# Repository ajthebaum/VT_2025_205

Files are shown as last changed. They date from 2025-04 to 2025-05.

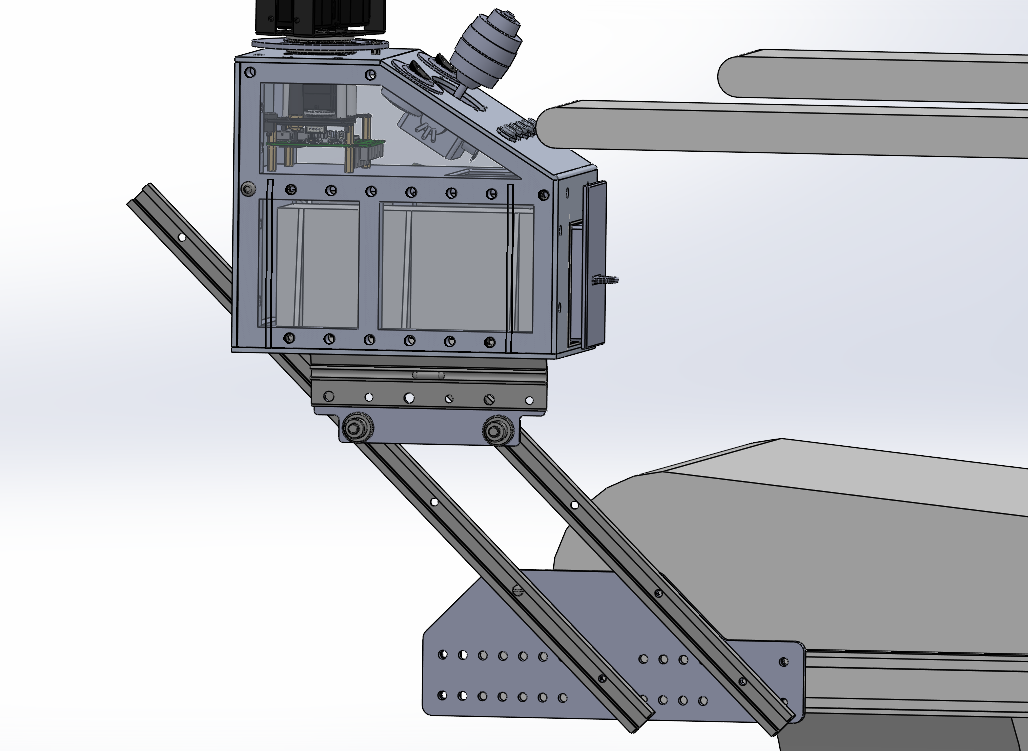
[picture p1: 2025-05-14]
CADFiles&Drawings/DXF and PDF Files/Reference Images/Fullview.png

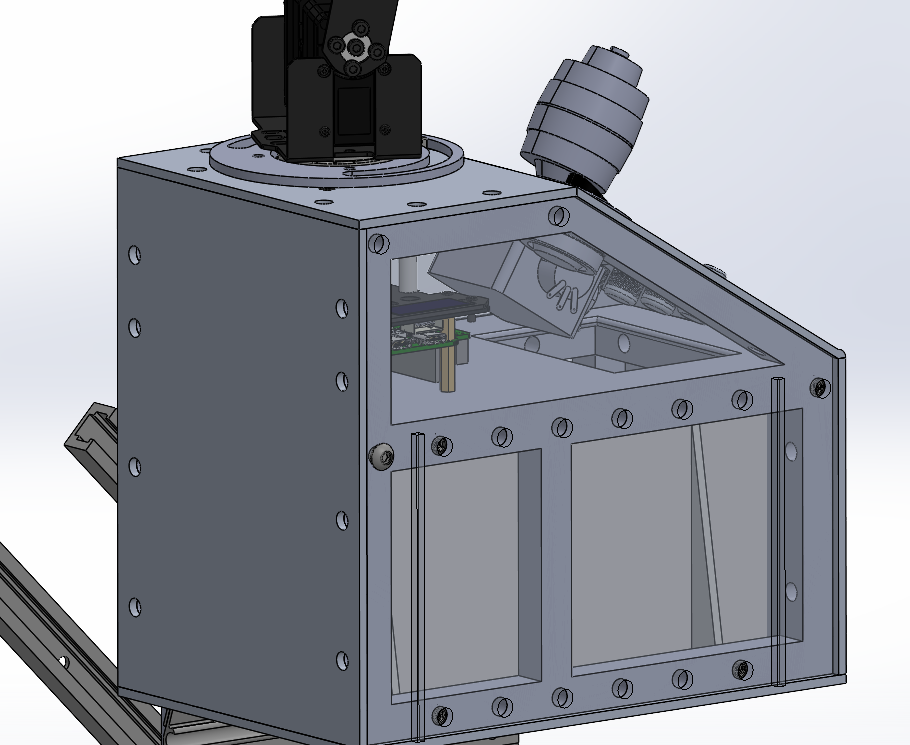
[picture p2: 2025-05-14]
CADFiles&Drawings/DXF and PDF Files/Reference Images/CaseView3.png

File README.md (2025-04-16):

# VT_2025_205
A collection of files for those interested in VT's team 205 Senior Design Project for the 2024-2025 year

VT's senior design team 205 is sponsored by Parent Project Muscular Dystrophy (PPMD). Our goal is to modify an off 
the shelf robotic arm for use on common motorized wheelchairs used by people with Duchenne muscular dystrophy (DMD).
It is intended for the project to continue past our senior year, and continue to refine and improve, as well as introduce new 
functions that may be of high value to people with DMD.

Currently, we are using the Waveshare Ro-Arm M2S, as well as an adafruit feather v2 along with a joystick, buttons,
switches, and LEDs. We are programming on the feather, formatting a JSON document that is sent over serial communication to
the board found on the Ro-Arm M2S, which then deserializes the JSON document and performs the corresponding robotic arm movement.
The code found on the Ro-Arm M2S board is provided by the manufacturer, and found in this repository is the code the team used
on the feather to read analog and digital signals and perform logic to update local coordinates.

We are not programmers, and have no formal training in programming (we're all ME's). There are refinements that can be made to our code that can 
significantly improve it, and we urge you to do so. We'd love to see this project continue, and see how people improve and adapt what we have done
to new problems, or new designs. Additionally, we are new to GitHub and are learning as we go. Feedback and advice are appreciated as we have a lot
to learn!

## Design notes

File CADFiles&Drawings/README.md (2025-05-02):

This folder contains the CAD parts, assemblies, drawimgs, and other files that were used to create the physical system that mounts on the wheelchair.
It may be necessary to rebuild the assemblies, refer to the assembly manual to see how its put together

These parts will be uploaded as we get time and once the final deliverables have been made

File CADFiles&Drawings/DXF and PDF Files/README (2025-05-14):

Files used for manufacturing parts on the laser cutter, CNC mill, and plasma cutter

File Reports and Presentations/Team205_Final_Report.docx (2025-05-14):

Proceedings of the 2025 Virginia Tech

Mechanical Engineering Senior Capstone Exposition

VTMECAP-2025

May 6, 2025, Blacksburg, Virginia, USA

VTMECAP-2025-205

# Assistive Robotic Aid for People with Duchenne Muscular DystrophY

Brooke Harrington¹, Cavan Moriarty¹, Omar Abuljobain¹, Justin Lee¹, Andrew Baum¹

¹Department of Mechanical Engineering, Virginia Tech, Blacksburg, VA

Abstract

DMD is a genetic disorder commonly found in men that deteriorates muscle tissue as they age, which progressively reduces mobility and requires those affected to use motorized wheelchairs for daily travel [1]. In addition to motorized wheelchairs, young adults with DMD often need devices that assist with upper body mobility. People with DMD would value an affordable, easy to control assistive robot that mounts on their wheelchair and provides two high value functions: operating elevator and handicap door buttons and bringing a drink to the user’s face.

To provide the two high value functions, team 205 utilized an off-the-shelf robotic arm, an Adafruit Feather V2 microcontroller, a joystick, buttons, switches, and other key electronics to develop a prototype for an affordable assistive robotic. Additionally, common materials and manufacturing methods were used such as 3-D printing, CNC milling, and laser cutters, to manufacture a mounting/containment structure for the assistive device. A prototype was fabricated, tested, and revised to ensure the device could accomplish the high value functions.

Team testing showed that the prototype met the requirements developed while conceptualizing a design, as well as user requirements such as size, safety, and functionality. Additionally, the prototype is able to complete its functions on instruments complaint with standards (minimum door width, button height requirements). End user testing showed that the prototype could complete the two high value functions, while being easier to control than other options on the market. Though the prototype was able to complete the two high value functions, improvements can be made that elevate user experience, ease of operation of the device, and sophistication of device functionality.

Nomenclature

3D Three Dimensional

ADA Americans with Disabilities Act

ANSYS Analysis System

CNC Computer Numerical Control

DMD Duchenne Muscular Dystrophy

DOF Degrees of Freedom

ESP Electronic Stability Program

FBD Free Body Diagram

FEA Finite Element Analysis

FOS Factor of Safety

GPIO General Purpose Input-Output

JSON JavaScript Object Notation

LED Light Emitting Diode

PCB Printable Circuit Board

PVC Polyvinyl Chloride

PPMD Parent Project Muscular Dystrophy

ROM Range of Motion

SPST Single Pole Single Throw

TR Technical Requirement

UI User Interface

1. INTRODUCTION

PPMD is a nonprofit organization that has been leading the fight against DMD since 1994, whose leading goal has been to ensure afflicted families have access to the latest assistive technologies through investment in research and development of pharmaceuticals and medical devices [1]. To help reach this goal, PPMD has sponsored senior design team 205 to develop an affordable and easy-to-use robotic aid by modifying a low-cost robotic arm and mounting it to commonly used wheelchairs. Although assistive devices may take various forms, the most optimal design was determined to be a robotic arm because of its ability to perform two high value functions: pushing an elevator/handicap button and retrieving a drink. Current robotic arms on the market that directly address DMD are often too expensive, some exceeding sixty-thousand dollars, and are difficult to control with more than six DOF [2]. Therefore, team 205 will provide users with DMD the key functions they require at a substantially lower cost with a less complex method of operation via a lower DOF system.

To simplify the design process of an assistive robotic device that could achieve the high value functions, the system was divided into three main subsystems: mechanical, electronic, and software. The mechanical subsystem included designing a mounting assembly that attaches the robotic system to a Permobil wheelchair, the most common wheelchair used in the DMD community. Additionally, the mechanical subsystem involved designing a case for sensitive electronics that also acted as a platform for the low-cost robotic arm and UI. The electronics subsystem consists of the RoArm’s PCB, the Adafruit Feather and protoboard, the UI (switches, buttons, joystick and LED), and the battery. When assembled, these components allow power to be distributed and used for control logic of the robotic arm. Lastly, the software subsystem found on the Feather reads signals from the UI and completed all necessary logic to update the coordinates, which were then formatted and sent to the RoArm PCB to be used for motor control. The software was also used to optimize control of the robotic arm and provide programmable functions desired by the end user.

Additionally, the team had to meet specific requirements determined by members from PPMD. The first requirement stated that the motorized wheelchair with the robotic system attached shall fit through an ADA compliant door, which has a minimum clearance width of thirty-two inches [3]. Second, the attached robotic system shall be able to press an ADA compliant elevator button and handicap door button, which are positioned between 35 and 48 in from the ground [4]. Third, the robotic arm and case shall be water resistant in the event that the user is caught in a rainstorm. Lastly, the system shall be easily attached and detached from the motorized wheelchair for transportation.

2. MATERIALS AND METHODS
  2.1 Mechanical
    2.1.1 Manufacturing Processes

Multiple manufacturing processes were required to fabricate the mounting and robotic system. For mounting, both the sliding and connecting plate were cut from an aluminum panel by a plasma cutter and CNC mill. Alternatively, acrylic panels were cut into their respective shapes using a laser cutter. Lastly, 3D-printing with ABS filament was used to create the required parts with varying infills and purposes.

3D-printed parts include the corner frame, battery case and cover, waterproofing well, cylindrical guide, end effector cover, pin, stopping plate, and armrest attachment. The battery case encapsulates the battery, which maintains its position at the lower half of the electronics housing by bolting to the bottom acrylic panel. The battery cover, waterproofing well, cylindrical guide, and end effector cover serve to waterproof exposed electronics by sheltering them or guiding water away from the electronics. The stopping plate was glued to the base servo-plate and provided a guide for a standoff. The standoff, bolted into the top of the electronics case, stopped the arm from rotating to undesired angles by colliding with the stopping plate, providing a mechanical safeguard as shown in Figure 1.

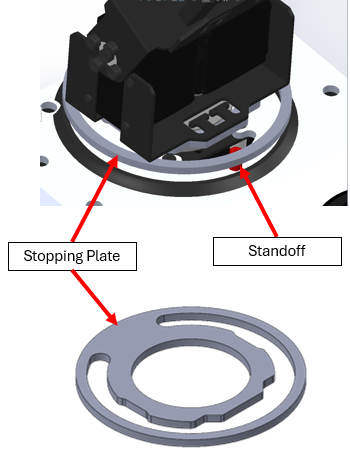
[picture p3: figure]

Figure 1: Mechanical Safeguard

Lastly, the armrest is an optional attachment that can be put in place of the front acrylic panel to provide support to the user’s arm during operation.

    2.1.2 Mounting

A Unitrack is a linear slide bolted to the side of a Permobil wheelchair, allowing for many extensions and attachments to be added. The mounting system is designed for quick, direct attachment to the Unitrack; however, the team only had access to a Jazzy motorized wheelchair. Therefore, an additional aluminum L-channel was needed to attach the Unitrack to the Jazzy wheelchair. In the ideal case of a Permobil, the mounting assembly involves a total of four aluminum components as shown in Figure 2: sliding plate, diagonal rails, connecting plate, and French cleats. The sliding plate is the primary point of contact to the Permobil that allows horizontal adjustment of the robotic system. The sliding plate is connected to the Unitrack via wing bolts to allow for easy adjustment and attachment/detachment of the entire robotic system to/from the Permobil. Next, the lower portion of the diagonal rails are attached to the sliding plate via pan head screws at an approximate forty-five-degree angle. The upper portion of the diagonal rails are connected to the connecting plate via a set of three fourths inch diameter locknuts, socket head screws, and square nuts. The connecting plate can slide along the diagonal rails which allows for simultaneous vertical and horizontal adjustment of the robotic system. Lastly, the connecting plate is attached to a pair of French cleats while another set is attached to the electronics case such that the robotic system can be easily removed from the mounting system by simply lifting the electronics case off the French cleats. To prevent the robotic system from being “bumped” off the French cleats, there is a 3D-printed pin that slides through the connecting plate and electronics case.

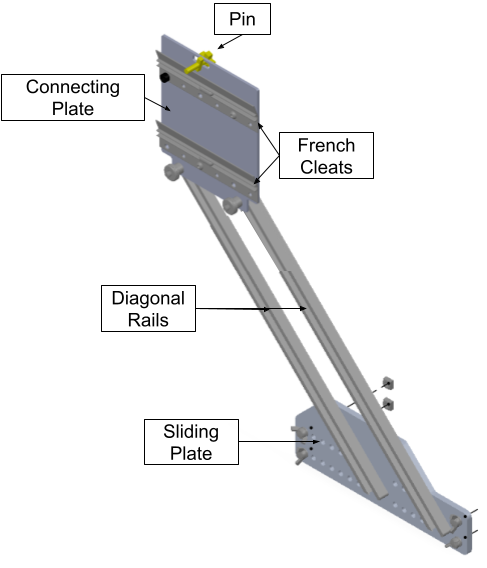
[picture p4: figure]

Figure 2: Mounting Assembly

The process for removing the system off the wheelchair involves removing the key that secures the electronics case and lifting the case off the French cleats. Then, loosening the wing bolts on the sliding plate, and sliding the mounting structure off the Unitrack will completely remove all parts of the system from the wheelchair. With only these two processes, the system is completely removed, meeting the end user requirement of a quickly installed and detachable system.

The ease of attachment for the mounting and robotic system was tested by timing the duration to attach the mounting system to the Unitrack, mounting electronics housing on French cleats, and placing the pin through the connecting plate slot and electronics housing. Ease of detachment was validated by sponsor testing, having a sponsor team member detach the system from the Permobil wheelchair without any prior instructions from the team. The stability of the robotic system in response to the mounting system was evaluated with root cause analysis as well as a sponsor assessment. The root cause analysis involved measuring the deflections of the diagonal rails when the robotic system was attached at different positions. Notably, this test was performed for the team’s Jazzy whilst the sponsor assessment was performed for the sponsor’s Permobil. The assessment involved visual inspection of the robotic systems response to static conditions and dynamic movement of the Permobil. While there were some deflections on the team’s Jazzy wheelchair, there were negligible deflections on the sponsor team’s Permobil wheelchair, which led the team to take no further action when addressing vibration, as it performed within expectations on the intended wheelchair.

    2.1.3 Electronics Casing

The electronics casing houses sensitive electronics, such as the lithium-ion battery, protoboard assembly, and ESP32, in addition to providing mounting points for the robotic arm and UI. The electronics housing is comprised of 3D-printed parts and laser cut acrylic plates.

As shown in Figure 3, the electronics casing has an internal structure that acts as the main point of connection to the robotic arm and acrylic panels. The robotic arm is bolted to the middle plate of the internal structure to a set of standoffs while the acrylic panels bolt to the sides of the internal structure with button head screws. These sides are lined with quarter-inch holes where nut inserts are heated and inserted to provide threading for the button head screws. Furthermore, the internal structure provides adequate space for sliding the protoboard into the pin headers of the ESP32 for a stable connection.

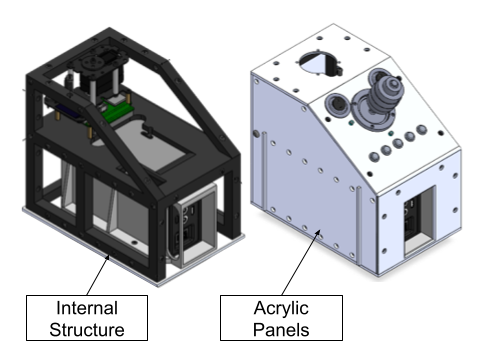
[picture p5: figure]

Figure 3: Electronics Casing

Since the system contains electronics and uses screws as fasteners, it is important to consider the maintenance process to ensure safe operation of the system. All physical components, including the acrylic panels and mounting structure, must be removed and inspected for physical and electric damage. Additionally, the electrical components must be inspected for loose wires, burns, or shorts, and fixed if necessary. Testing will ensure that maintenance activities do not result in system removal from the end user for an extended period, as the end user relies on the system for daily, repetitive tasks. A time limit of three hours was estimated to complete these maintenance activities and tested after full system assembly.

    2.1.4 Robotic Arm

The Waveshare RoArm-M2-S robotic arm was purchased from a third-party vendor and later modified to meet the team’s needs. Initially, the arm was selected as it satisfies the team payload capacity, accuracy at maximum reach, and price requirements. Choosing an arm that satisfied the requirements from the team’s analysis was important in developing a system capable of completing the two high value functions. Once acquired, minor modifications were made such as rotating the end effector ninety degrees as well as rotating the base of the arm ninety degrees to fit the axes of our coordinate system; effectiveness of these changes were verified through testing system operation.

The payload capacity of the end effector was tested by increasing the applied load at the end effector by 100 g each time the robotic arm successfully completed the drinking function; further details on drinking function can be found in Section 2.3. Alternatively, the accuracy of the robotic arm at maximum reach was tested by measuring the horizontal and vertical precision of the end effector position relative to a 35-inch and 48-inch mark. Additional details regarding the test for accuracy can be found in Section 3.2.

    2.1.5 Water-resistant Design

To aid in the water-resistant design of the system, a PVC sleeve, 3D printed end effector cover, 3D printed well, and 3D printed cylindrical sleeve guide were utilized. The end effector cover is meant to protect the end effector servo motor for a short duration in light rainfall. The sleeve acts as an elbow joint cover on its own, but when used with the cylindrical sleeve guide and well, can help protect the lower half of the system, ranging from the elbow servo motor, down to the base servo-motor inside the casing unit.

  2.2 Electrical
    2.2.1 Protoboard

A generic protoboard was used as a connection point for all electronic components which included the ESP32, the Adafruit Feather V2, and the UI. The UI was soldered directly to the protoboard, while the Feather was inserted into corresponding headers that were soldered to the protoboard. Lastly, male headers were soldered to the protoboard and would plug into the female headers of the RoArm PCB, which allowed for serial communication between the Feather and RoArm, and power distribution.

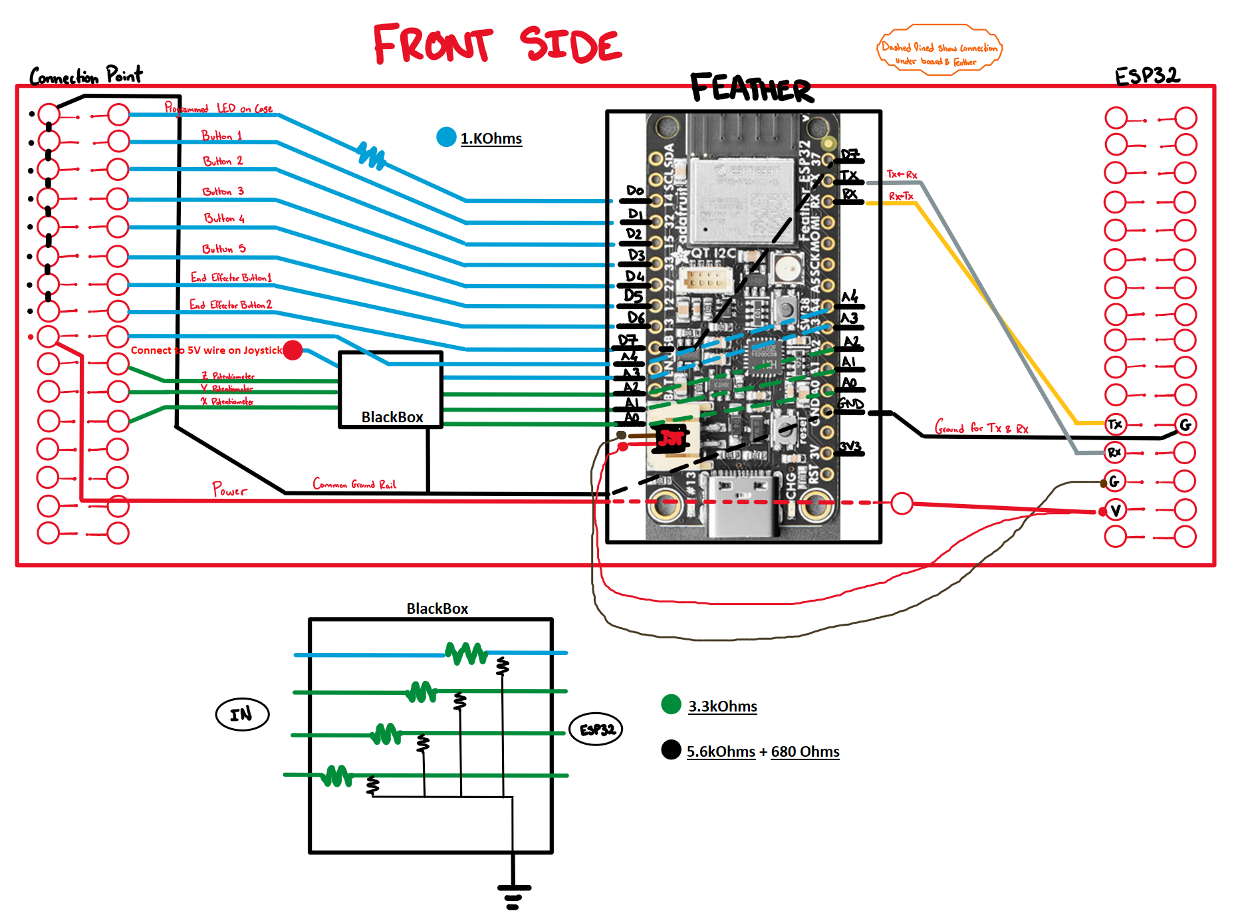
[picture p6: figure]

Figure 4: Protoboard Layout with Feather

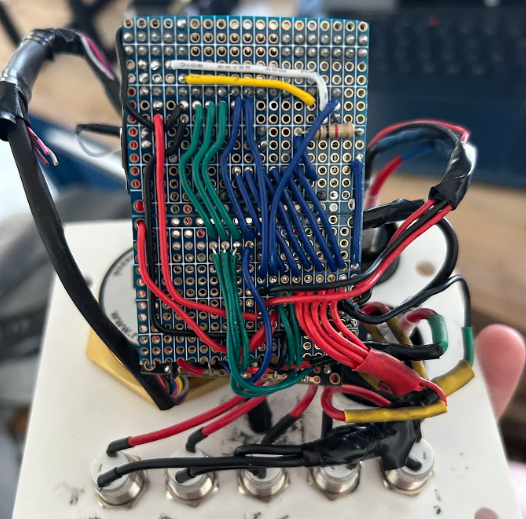
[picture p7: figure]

Figure 5: Protoboard with Solder Connections to Switches, Buttons, and Joystick

    2.2.2 User Interface

The UI contains a three-axis, two-button, Ruffy controls hall effect joystick, five momentary buttons, two SPST switches, and one white LED. Two LEDS beside the switches were removed due to electrical complications that could not be resolved before project completion. The switches were used to enable system and joystick control, and the joystick was used for manual manipulation of the robotic arm. The buttons were used for programming saved locations for later recall, and the LED was used to convey system status to the user. All UI subsystems were mounted on the diagonal plate of the electronics casing, where they would be accessible to the person in the motorized wheelchair as seen in Figure 6.

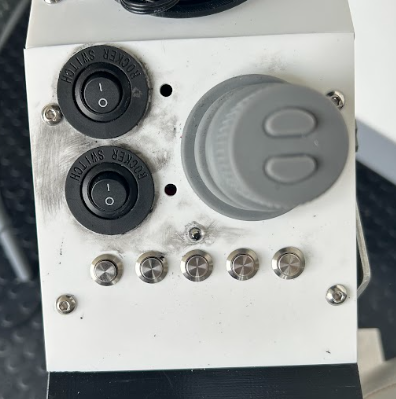
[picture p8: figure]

Figure 6: User Interface (Left – Switches, Right - Joystick, Bottom – Buttons, LED above 3rd button)

    2.2.3 Battery

A 38,400 mAh battery was used to power the robotic arm and all electronics used in the system. The battery is contained in the base of the electronics case and has an LED display showing capacity. The battery also has a switch for powering on and off the system, and a USB port for other attachments. 12 V is routed from the battery to the ESP32 on the robotic arm, which then powers the Feather and protoboard, then the protoboard distributes 3.3 V and 5 V to systems on the UI.

To determine the required battery size, the time at max output and time at minimum output per day were estimated and multiplied by the amperage of these operations then summed to determine the necessary capacity for a battery to last 1 day. Using the frequency of buttons as 30 times a day with a time of 15 sec and the frequency of drink as 30 times per day with a time of 20 secs, max current I of 5 A and min current Imin as 0.2 A, the required battery capacity was determined to be 6200 mAh.

time_(max) = ((freq_b *time_b )+ (freq_w *time_w ))/3600 | (1)
time_(max) =0.2917 hours
time_(min) =24-time_(max) =23.7 hours | (2)
req_(mAh) =((I*time_(max) )+(I_(min) *time_(min) ))*1000 | (3)
req_(mAh) = 6200mAh

The battery selection provides adequate capacity (6.2 times estimated value), which accounts for any differences between estimated values and actual values for the tasks above, and variance in use from different end users.

  2.3 Software
    2.3.1 Waveshare ESP32

The Waveshare RoArm comes equipped with a PCB that contains motor drivers and handles serial communication. This PCB is sold with preinstalled code that can be modified; however, the team opted out of modifying the RoArm code since one of the project goals was to be easily replicable. The code on the RoArm PCB reads a JSON object that contains position data from the serial communication (transfer-TX and receive-RX) pins, which the RoArm then deserializes and turns into motor control. Since the team did not modify this code, an Adafruit Feather V2 microcontroller was used for all logic and coordinate updates.

    2.3.2 Adafruit Feather V2

The Adafruit Feather V2 is an ESP32 based microcontroller equipped with GPIO pins that are used for digital and analog communication with other electronic components. Communication between the Feather and the RoArm PCB uses the “RX” and “TX” pins as seen in Figure 4, which are wired inversely between the boards. The GPIO pins on the Feather are used to take inputs from the switches, joystick, and buttons, and output to the LED. The code on the Feather uses these readings to update the coordinates or call specific functions such as the automatic drink function. Specifically, the joystick is used to manually update the coordinates of the end effector, and the buttons are used to recall specific coordinates that have been previously programmed by the user. Once the user wants to move the end effector, the coordinates are formatted into a JSON object that contains the numeric identifier for the type of control, the cartesian coordinates of the end effector destination, and the speed at which the arm should move. An example is provided below. This data is sent across the serial communication pins, where the RoArm uses the numeric identifier and position data to calculate motor movements. The numeric identifier used for all code on the feather was “1041” or “104”, which specifies that the data contained in the object are x, y, z, and end effector pitch, t, positions (104 allows you to specify a “spd” variable in the object, where 1041 does not, both produce the same linear movement between current and goal points).

The following code is an example of what is written in the Feather:

StaticJsonDocument<200> curposdoc;

curposdoc["T"] = 104;

curposdoc["x"] = curxpos;

curposdoc["y"] = curypos;

curposdoc["z"] = curzpos;

curposdoc["t"] = curtpos;

curposdoc["spd"] = 0.2;

serializeJson(curposdoc, Serial1);

Serial1.println();

What the RoArm receives from the Feather:

{“T”: “104”, “x”: curxpos, “y”: curypos, “z”: curzpos, “t”: curzpos, “spd” = 0.2}

These objects that contain the position data are continuously updated in the Feather and sent to the RoArm to move the end effector position. Optimizations in the code that sync the transfer speed (between the Feather and RoArm) and the coordinate update speed ensure that equal increments of coordinates are sent with each data transfer.

3. RESULTS AND DISCUSSION
  3.1 Results of FEA
    3.1.1 Free Body Diagram

To estimate the mechanical load experienced by the case and mounting structure, a FBD was developed using estimated forces and moments generated during arm operation, which includes the weight of the arm, case, battery, and load, as well as the moments generated by the load and arm and full extension. The model assumed an extreme use test scenario in which the arm is fully extended with a payload at the end effector. This condition was selected to ensure the support structure can withstand maximum mechanical stress.

The total moment applied to the mounting assembly was found to be 4.03 Nm, acting in the counterclockwise direction. The corresponding force at the mounting point, excluding the weight of the case, was determined to be 20.16 N. The contribution of dynamic human interaction was considered negligible in the FBD but was evaluated separately for safety margins. All forces were applied at the interface between the arm base and the vertical support tracks. The calculated forces were then used as the input for subsequent finite element analyses to verify the structural integrity of the electronics casing and mounting assembly under expected operating conditions.

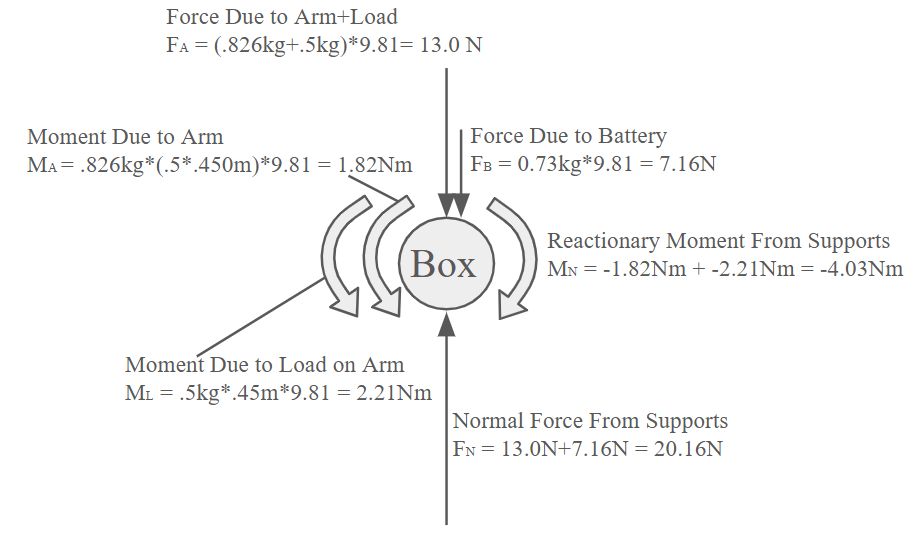
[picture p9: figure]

Figure 7: Free Body Diagram of System

    3.1.2 Engineering Analysis

Following the force and moment estimations from the FBD, a structural FEA was conducted using ANSYS to evaluate stress concentrations and deflection behavior in the electronics casing and mounting assembly. The materials used in the construction were primarily 6061-T6 aluminum alloy, selected for its high strength-to-weight ratio and availability. The alloy has a yield strength of 275.8 MPa, which served as the basis for FOS calculations. Under the maximum loading conditions, the highest observed stress concentration was 48.44 MPa, occurring in the T-track that mounts to the vertical rails as seen in Figure 9. This yielded a conservative FOS of 5.69, which indicated the design was capable of withstanding operational forces without material failure.

Deformation analysis revealed a maximum deflection of 1.62 mm at the edge of the case. This displacement was well within the design tolerance and did not interfere with arm accuracy, which had a resolution requirement of ±10 mm at full extension. Additionally, rotational and positional accuracy for each joint was analyzed based on encoder specifications. The final cumulative error was estimated to be <0.8 mm, confirming that the structural deflection would not compromise system precision. These results validated the mechanical robustness of the mounting architecture and confirmed that the system can maintain both strength and accuracy throughout normal use.

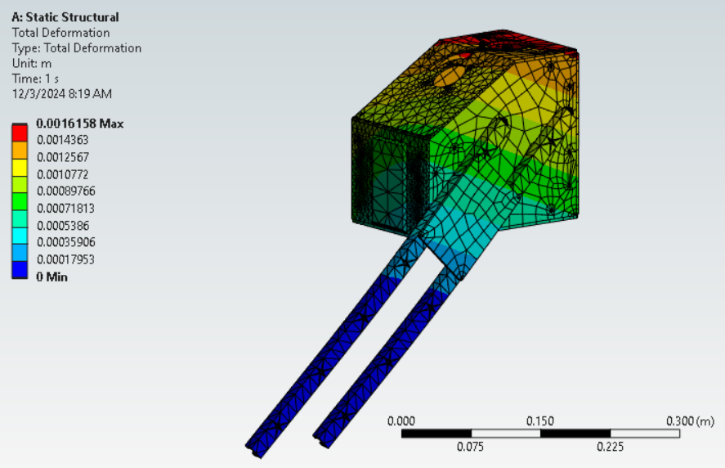
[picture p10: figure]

Figure 8: Ansys Static Structural Analysis of Deformation

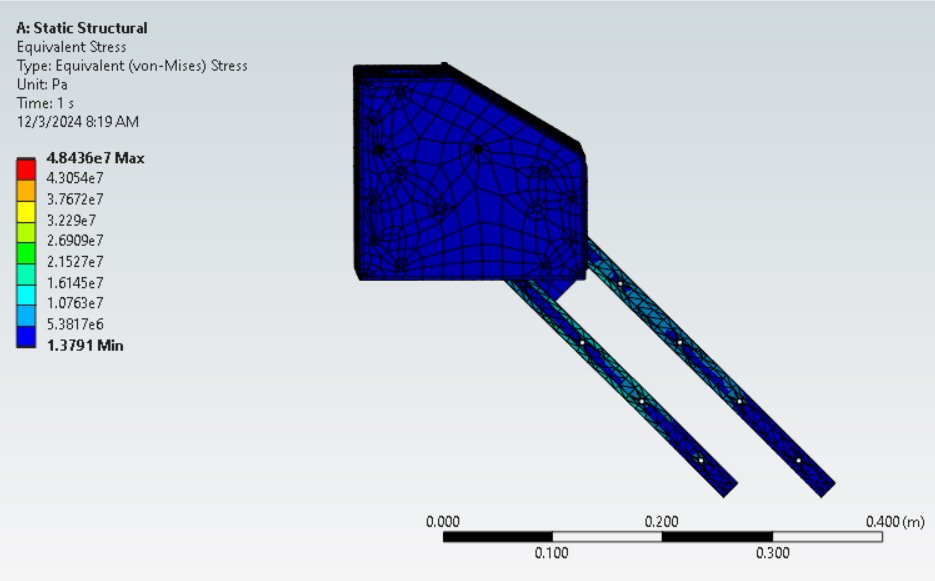
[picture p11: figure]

Figure 9: Ansys Static Structural Analysis of Stress

  3.2 Results of Test Plans
    3.2.1 Installation Test

An installation test was conducted to determine the ease of installation in accordance with TR 3.0.0: The robotic aid shall be installed in less than 1 hr. The test was performed by timing the assembling of the mounting system to the wheelchair Unitrack, placing the French cleats of the electronics casing onto the French cleats of the mounting system, and finally securing the electronics casing to the mounting assembly with the 3D-printed pin. Lower times indicated an easier installation process. The limit for passing this test estimated at 1 hr, and the test was completed in under 1 min at 58.52 secs. This overestimate of installation time was due to multiple design simplifications that improved the installation process by decreasing the amount of assembly required to completely install the system.

    3.2.2 Maintenance Test

A maintenance test was completed to evaluate the time it takes to perform standard maintenance activities, which is important since removal of the system from the user for an extended period of time (3 hrs) is non-ideal, as the user needs the system for daily tasks (TR 3.1.0). Maintenance activities included inspection of all physical structures of the system, inspection of all wire connections and heat shrink, and inspection of the PCB and protoboard for any burnt components. Any damage or broken components that were fixed were included in the test time. The limit for passing was 3 hrs, the expected value was estimated at 1 hr, and the actual value was 22 mins and 53 secs. The system passed the test with a minor electrical tape fix, and it is recommended that a retest be completed after significant use or after six months.

    3.2.3 End Effector Max. Load Capacity Test

The end effector max. load capacity test addresses TR 1.1.4: the arm should be able to bring a drink weighing 470 g to the user, which verifies the robotic arm’s ability to meet the key function of retrieving a drink to the user. This test was performed by increasing the weight of the drink by 100 g every time the robotic arm successfully completed the drinking function. For each execution of the drinking function, a visual inspection of the system’s performance and stability determined whether the robotic arm performed satisfactorily or if the maximum weight limit had been reached.

The results determined that the robotic arm is able to hold a weight of 500 g when extended to its maximum and a weight of 600 g when at close range. Thus, the robotic arm exceeds expectations, meets TR 1.1.4, and is able to successfully retrieve a drink. The weight of the drink includes the combined weight of the liquid, container, and portable cupholder.

    3.2.4 Accuracy Test

An accuracy test was performed to ensure the system was accurate to 10 mm at full extension, stated as requirement TR 1.3.2. This requirement was developed from the ADA button size and height standards, stating the minimum diameter of an elevator button to be ¾ in, and the height from ground to be 35-48 in [4]. This test utilized a tape measure, calipers, the assembled system on a motorized wheelchair, a whiteboard imitating a button wall, tape, and a whiteboard marker to mark the necessary points. At the lowest incremental movement translated from the joystick’s X and Y axis, one unit was moved right from the initial mark set at 35 in from ground. A second point was marked, and the end-effector was once again incrementally moved one unit upward in the Z direction. Once three points were marked, the same procedure was executed 48 in from ground.

Initial results ranged from 5 mm to 14 mm, implying the system can still press ADA complaint buttons; however, it fails the team’s accuracy requirement of 10 mm.

To resolve the initial failure, the speed of position incrementation in the code was changed to 40 ms, such that the incrementation of the position matched the data transfer rate. Syncing these tasks resulted in an accuracy improvement, now ranging from 4 mm to 8 mm, thereby passing the test.

    3.2.5 Restricted Motion Software Safeguards

To ensure safe operation around the user, particularly preventing unintended contact with the user's arm or torso, the team implemented software-based spatial restrictions into the robotic arm’s control system. This safeguard was developed in response to requirement TR 5.2.0, which specifies that the system must include physical or software constraints that prevent the robot from reaching undesired locations. The Feather was programmed to actively monitor the robot’s spatial coordinates—specifically the x, y, and z positions—using magnetic encoder feedback from the Waveshare RoArm motors. The code defines a restricted region in the operating environment, primarily an angular zone ±30° on either side of the UI as seen in Figure 10, where the end effector is prohibited from entering. This safety zone was determined by ergonomic analysis and sponsor feedback, ensuring the robot would never encroach on the user’s hand space during operation.

The restricted motion logic is embedded in the coordinate update routine. If an input command—via joystick or recalled motion function—would move the end effector into a forbidden zone, the command is overridden, and the motion is aborted before transmission to the RoArm system. During the test, the software safeguard was verified across minimum, medium, and maximum speed settings. At all tested velocities and configurations, the robot’s movement remained strictly within allowed regions. As a result, the software safeguard not only fulfilled TR 5.2.0 but also made the reliance on a mechanical limit a redundancy rather than a necessity. The success of this test highlights the effectiveness of embedded software control in maintaining operational safety, especially for users with limited mobility who rely on consistent, predictable system behavior.

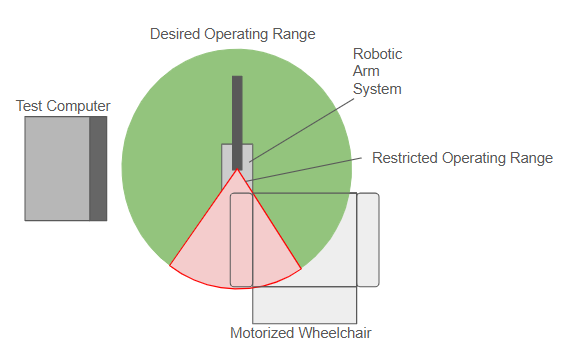
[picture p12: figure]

Figure 10: Diagram of Restricted Motion Test

  3.3 High Value Functions
    3.3.1 Automatic Water Function

An automatic water function was provided in the Feather code, which allows the user to program a “drink” location on the wheelchair and a “user” location where they want the drink to remain for use. The user will additionally program two “safe” points that the system will path through to ensure proper clearance between the drink and the case. Holding the second button on the UI for five seconds will enter “programming” mode for this button, where the user will program these four points. Then pushing the second button momentarily will run the function, moving to the positions saved by the user. Additional logic, such as when to open the end effector and how to move between points, is done within the code and is not programmed by the user. To change this behavior, the user must change the function in the code, which is provided online in a GitHub repository. Currently, the function is operable and works for specific mounting locations of the drink; however, testing on the intended wheelchair was not possible due to mounting interferences with other necessary equipment. Since each person's wheelchair is different, it is ideal to have the cupholder at roughly the same height as the case due to robotic arm capabilities, but more research should be done on an ideal location.

      3.3.1.1 Code Progress

The code is broken into three parts: manual joystick operation, button operations, and safety checks. Manual joystick operation reads the values of the potentiometers in the joystick and compares against limits to increment the local coordinates, which are formatted into a JSON object and sent to the robot.

The button operations use a general button reading function, which passes the button variables into the function, and calls the corresponding programming or recall function for the robot depending on how long the button is pushed for. This framework can be used for additional functions, or to change existing functions, as the movement functions are independent of the button reading framework. Button operation is further discussed in 3.3.2.1.

Lastly, spatial safety features have been implemented to prevent the robot from moving erratically. There are limits on the end effectors maximum and minimum distance from the origin, which prevent the robot from swinging too quickly and hitting other objects or people. There is also a restricted area that spans 60° above the UI as discussed in 3.2.5, which prevents the end effector from hitting the user’s hand while operating the joystick. The last safety measure defines the coordinates of the case and does not allow the end effector to move into this area, so the system does not break itself. Together, these safety features define the operating space of the robot and prevent it from harmfully interacting with itself and its environment.

    3.3.2 Elevator Button Pressing
      3.3.2.1 Ready Positions

One key goal for the system was the ability to store and retrieve position data throughout power cycles. The Arduino “preferences” library was used, which stores data to non-volatile memory using a preferences namespace and keyword. By holding a specific button down for five seconds, the user can enter the “programming” mode and move the arm to the position they would like to store. By pushing the same button momentarily, the user will now store this location and exit programming mode. To recall this position at any time, the user can momentarily push this button, and the arm will move to this stored position. Three buttons are compatible with this operation, firstly, button one programs a “ready” position that is ideally used to move the arm up and in front of the case. Button three and four are used to program two different stow positions. Together, the user can save three unique positions, and one function (automatic drink function), which stores four positions.

      3.3.2.2 Accuracy

Accuracy of the system was a high priority when making design choices, which was reflected during testing through focus on end effector accuracy and spatial safety. The accuracy of our system is determined by three factors: the code, the servo accuracy, and the structural stability of the assembled system. By syncing the coordinate update speed with the data transfer speed, user inputs have been converted to single increments in position data, thereby optimizing the system by preventing overshoot of desired position. Additionally, the distance the joystick is moved from its neutral position is utilized for variable speed control of the robotic arm, where pushing the joystick further from the default position results in quicker movement of the arm.

The Waveshare RoArm was selected because of its servo motor accuracy, advertised to have a resolution of 0.088 ° , translating to a single (base) motor accuracy of ±0.78 mm. As system complexity increases with more motors, the accuracy will likely decrease, but tests show the value remains within the team’s specified accuracy for performing high value functions.

The last factor that effects accuracy is system structural stability, which is a concern for end effector accuracy as the weight shifts or adjusts, causing deflection. Initial FEA showed that deformation under load is not significant enough to affect the end effector’s location, which was verified when installed on the intended Permobil wheelchair through inspection.

Proper design of these three factors minimized errors in accuracy, which was observed when the team and end user were able to successfully navigate to and press a button.

      3.3.2.3 End Effector Modification

Several modifications to the end effector were made so that the two functions were better performed, including rotating the end effector ninety-degrees, glueing a rubber pad to the tip of the end effector, and 3D-printing a cover. Previously, the end effector was oriented to open about the z-axis of a standard cartesian coordinate system. The end effector was rotated so that it opened about the y-axis. Opening about the y-axis resulted in better gripping the horizontal handle of the portable cupholder, allowing it to better perform the drinking function. It was observed that the end effector tended to slip when pressing a button, so a rubber tip was glued to the end effector for better grip and continuous pressure on button surfaces. Lastly, the 3D-printed cover was added to the servo that actuated the end effector, shielding from possible splashing or sudden rain.

  3.4 Open-Source Planning
    3.4.1 GitHub/Google Drive

All files related to the purchase, design, and construction of the project are available on a GitHub repository as part of PPMDs goal to have the system be available for hobbyist and future teams to work on and improve. The repository also includes a manufacturing manual that provides an estimate for third party manufacturing based off the team’s design choices, in case the user does not have their own 3D printer, CNC mill, or laser cutter. Additionally, the repository includes assembly and operations manual, an itemized bill of materials, and CAD files that are necessary for system construction.

In addition to the GitHub repository, a google drive has been created that contains images of the project, videos of testing by the team and end user from PPMD, and tutorials videos made to aid the operations manual when describing programming and recalling locations.

The hope of PPMD is that making this project open source will allow the community to continuously improve the design and functions after the end of this project and add new features that would be beneficial to a person with DMD. Additionally, the GitHub repository will be used for future teams if the project continues or is revamped in years to come.

    3.4.2 Bill of Materials

Throughout the duration of the project, a multitude of materials were purchased for initial testing, backup materials if something breaks, and final production materials which summed to a total cost of $2114.45. This value represents the total amount spent by the team, including shipping and taxes, but excluding manufacturing costs as all necessary parts were made in house. The total cost to replicate the system is $1147.62 when considering direct materials and manufacturing costs through third parties and excluding shipping and taxes. Overall, both cost estimates are less than half of the team’s budget of $5000, and a fraction of the cost of other market solutions, meeting the teams goal of developing an affordable system that is available to a larger group of people with DMD.

4. CONCLUSION

The system can complete the two high value functions desired by the end user: pushing elevator buttons and bringing a drink to the user. Additionally, the system has safety measures put in place to prevent the robot from harming the user or those around the system. Though the system meets the standards defined by the team, validated through testing, refinements and improvements can be made that elevate the end user experience and provide better assistance for everyday tasks.

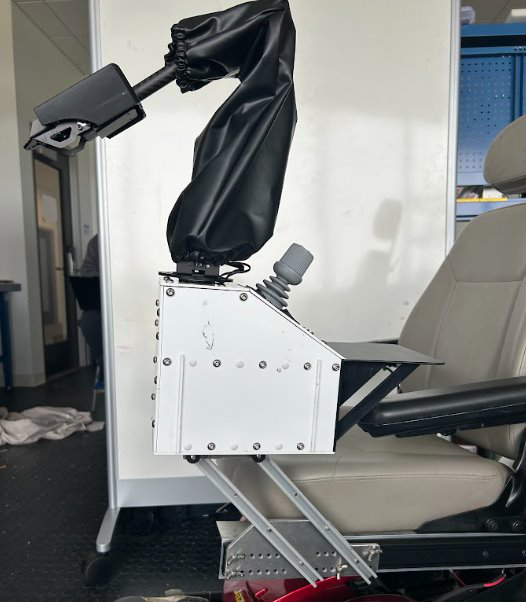
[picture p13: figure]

Figure 11: System Assembled on Jazzy Wheelchair

ACKNOWLEDGEMENTS

The team extends gratitude to Mr. Keith Van Houten and PPMD for sponsoring the project, as well as the PAAC Committee from PPMD for working with the team and providing valuable feedback to ensure a quality prototype.

Many thanks to Mr. Stephen Moyer and Mr. Jim Hess for advising team 205 through the duration of the project, and for providing crucial insight and guidance when the team was struggling.

A special thanks to Colin Werth, for allowing the team to visit and get feedback from Colin’s design testing, and for continuously engaging with the team through the duration of the project. Thank you to Mr. and Mrs. Werth as well, for allowing the team into their home and for their hospitality during the visit.

Lastly, a thanks to Mr. Richard Henegar and Ms. Kristie Yelinek for helping the team secure a test wheelchair, and for guidance when the team was unsure about certain technologies used for the project.

REFERENCES

[1] “About Duchenne” (2020), Parent Project Muscular Dystrophy. https://www.parentprojectmd.org/about-duchenne/ (Accessed Dec. 10, 2024).

[2] ROBOTS. “JACO” IEEE, https://robotsguide.com/robots/jaco (accessed Apr. 28, 2025).

[3] U.S. Access Board. 2024. “Chapter 4: Entrances, Doors, and Gates.” United States Access Board, https://www.access-board.gov/ada/guides/chapter-4-entrances-doors-and-gates/. (Accessed May 6, 2025).

[4] U.S. Access Board. 2024. “Chapter 4: Elevators and Platform Lifts.” United States Access Board, https://www.access-board.gov/ada/guides/chapter-4-elevators-and-platform-lifts/. (Accessed May 6, 2025).

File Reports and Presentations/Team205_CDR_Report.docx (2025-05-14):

205 - Assistive Robotic Aid for People with Duchenne Muscular Dystrophy

Sponsor: Parent Project Muscular Dystrophy (PPMD)

Sponsor Contact: Mr. Keith Van Houten

Faculty Advisor: Professor Stephen Moyer

ME 4015 – Engineering Design and Project

Submittal Date: 12/10/2024

Members and Roles:

Brooke Harrington - Team Lead

Andrew Baum - Secretary

Omar Abuljobain - Treasurer

Justin Lee - Operations Assistant

Cavan Moriarty - Programming Lead

Table of Tables

# Executive Summary:

Duchenne muscular dystrophy (DMD) is a genetic disease that effects mainly men, causing muscle degeneration over time which progressively weakens those affected as they age [1]. People affected by DMD use motorized wheelchairs for travel, and often require assistance from a caretaker, or assistive technologies to complete daily tasks such as drinking from a bottle and operating elevator/ handicap door buttons. Although there are mechanical aids to help those affected, the value these aids provide lessens as the disease progresses and the user becomes weaker, necessitating new devices that provide an improved range of motion (ROM) assistance [2]. Progressive muscle weakness of DMD requires design, integration, and testing of an assistive robotic aid that provides ROM assistance to people with DMD, with a focus on tasks including operating an elevator button, operating handicap door buttons, and bringing a drink with a straw to the user’s mouth.

The most prominent solution on the market is the Kinova Jaco assistive robotic arm. The Jaco has six degrees of freedom (DOF), three of which make up the arm, and three that make up the wrist. The Jaco is operated by the wheelchair joystick and uses existing batteries on the wheelchair to power the robotic arm [3]. The combination of the Jaco’s high DOF and overlapping joystick controls make operating the arm unintuitive and complex, providing reduced value to a person affected by DMD. Additionally, the arm's integration of controls and power source into the wheelchair's controls and power source makes travel difficult as airport policy requires the arm to be taken off the wheelchair. Finally, the Jaco costs roughly $60,000 which insurance does not cover, making the Jaco a device not acquirable for most people. To provide ROM assistance to people with DMD, team 205 will modify a low-cost robotic arm such as the Waveshare which offers key features at an affordable price of ~$189.99: simple controls due to four-DOFs, reach of ~19.5 inches, high torque capacity of 0.5kg, and compact design. With this, a mounting structure and a case will be fabricated to hold the Waveshare, and any additional electronics, to fit onto common motorized wheelchairs such as the Permobil M3 Corpus. The solution is novel due to its simplified control mechanisms at an affordable price, as well as safety features like physical limiters that protect the user from being hit by the robotic arm.

The current system designed by team 205 is positioned with the base of the Waveshare robotic arm about 35 inches off the ground, making it nearly level with the lowest elevator button complaint with The Americans with Disabilities Act (ADA) standards outlined in chapter 4 §407.4.6 [4]. The robotic arm has a max reach of about 20 inches, meaning that at full extension the arm can reach the highest elevator button complaint with ADA standards (12-inch span from the lowest to highest button, with the center of the lowest button at 35 inches above the ground and the top of the highest buttons at 48 inches above the ground). In addition to reaching elevator buttons, the system is mounted in a location that is easy to control for people with DMD, with the joystick positioned in front of the armrest, and adjustment capabilities for the entire system. The current design also includes physical limiters to address risk of hitting the user and has gaskets lining the exposed edges of the case so that when assembled, the system is waterproof. The system is powered by a power bank that can be charged through a wall outlet and does not need to be removed during charging, which is important for people with DMD who don’t have the mobility or dexterity to disassemble the system for charging. While the current system meets the requirements of the end user, it still needs to be manufactured and tested.

Following winter break, the team will begin prototyping the system by 3-D printing the case, allowing for multiple iterations to be made as challenges arise, and fitment testing to occur through each iteration. The 3-D printed case will be used for testing purposes and iteration; however, the team recommends that the system be built out of aluminum for durability and stability in future years. While manufacturing the case, the team will also focus on developing code and testing the Waveshare robotic arm to ensure that the team can control the robotic arm through the joystick. Lastly regarding manufacturing and assembly, the team will modify a donated jazzy wheelchair to represent the Permobil M3 for fitment and system testing. Outside of manufacturing and assembly, the team will refine test plans for the system and begin testing once specific parts of the system are complete. The team will also schedule time to meet with end users and get real-time feedback for small changes to be made before Capstone Expo. The team expects to have a prototype assembled by the beginning of March and meet with end users within the following weeks of prototype completion, leading to refinement during March and April in preparation for Expo in May.

# Introduction:

As previously mentioned, individuals with DMD suffer from muscle degeneration that progresses as they age. This progression typically begins within the lower limbs and spreads into the upper body, effectively limiting their mobility, thus, requiring aid from caretakers or assistive devices that are currently too expensive, bulky, complex, and difficult to remove. For these reasons, team 205 has been tasked with developing an affordable, easy-to-use robotic aid that can help with everyday tasks. More specifically, the team must purchase and modify a low-cost robotic arm to perform high value functions such as pushing an elevator/handicap door button and bringing a cup to the user’s face. As discussed with PPMD, team 205’s solution not only resolves the concerns of current assistive devices but also ensures user independence.

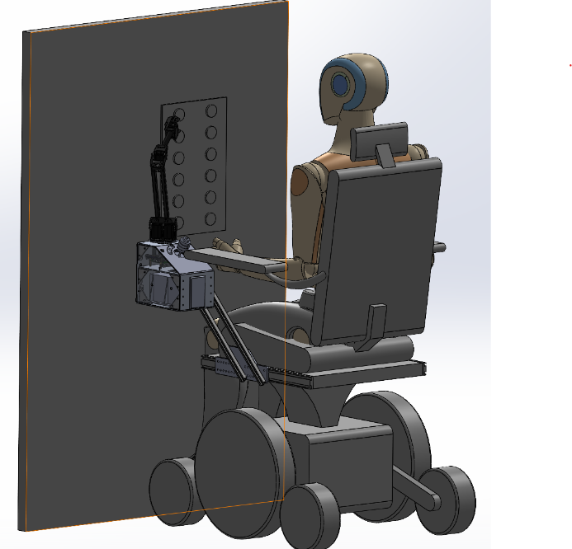
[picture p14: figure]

Figure 1. High Level Solution Diagram

# Solution Summary:

Key features of the computer aided design (CAD) include the case that houses the electronics (ESP32 and power bank) and provides mounting points for the Waveshare robotic arm, joystick, and vertical rails. The system mounts to a Unitrack [5]: a linear slide that comes bolted with a Permobil wheelchair that will serve as the main point of connection between the wheelchair and the robotic aid. A mounting plate secures the vertical rails attached to the case to the Unitrack. Together, these components allow the customer to, via the robot arm, interact with their environment in a relatively cheap, easily removable, completely contained robotic aid. Figure 2 shows a CAD model of the entire system consisting of the case, mounting system, Permobil wheelchair, Waveshare robotic arm, and joystick. This image will be used as a reference when viewing the individual parts and putting sizes into perspective.

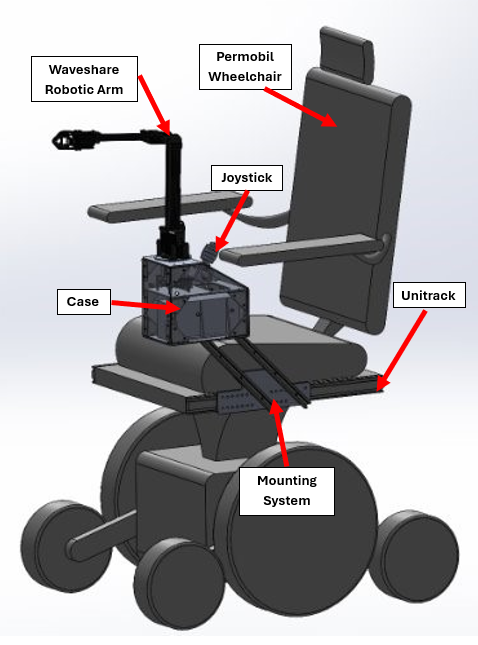
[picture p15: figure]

| Figure 2. Robotic Aid CAD Assembly

Figure 3 displays the case and its mounted electronics. Previously the case was modeled to represent the maximum packaging envelope measured with dimensions provided by PPMD members and the ADA requirements for a minimum door width. The case was then adapted to a minimum size (from 3,704.2 cubic inches to 277.7 cubic inches - L8.22 W5.25 H7.25) based on the dimensions of the electronics, modified to mount the joystick and robotic arm, and compared to the previous model to ensure it fits within the maximum footprint. The holes that allow the case to attach to the mounting system are mirrored on each side of the case, allowing the case to be mounted on either side of the wheelchair. To ensure both structural integrity with a lightweight design, the case will be made from 1/8-inch aluminum. The simple case design allows for the use of aluminum sheets, which are malleable and easily cut, simplifying the manufacturing process. This material choice also considers the heat dissipation qualities of aluminum as it is a metal with a relatively high thermal conductivity at 237W/m∙K [6]. This means that the case would be able to absorb the heat generated by the electrical components inside and dissipate it into the cooler outer environment. Furthermore, the case features ventilation slots on the bottom plate to allow any excess heat to escape without risking water infiltration.

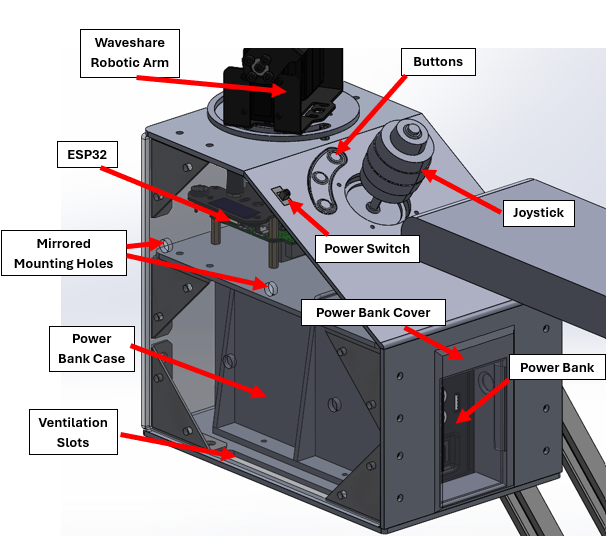
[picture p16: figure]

| Figure 3. Case CAD Assembly

The power bank is a 12V 38400 milliamp-hour (mAh) battery that allows the user to plug in a charging cable without having to remove the power bank. It also features a power switch that can be used as an emergency shutoff switch if needed. The power bank is held firmly in place by a 3D-printed case made with ABS filament, which is bolted to the bottom of the case. Furthermore, there is a plate that slides in front of the power bank called power bank cover, mitigating the chance of a water hazard. Mounted to the diagonal plate are the 4-axis joystick, buttons, and power switch that serve as the controls for the arm. The joystick is mounted at an angle similar to joysticks already installed on wheelchairs for a natural method of controlling the robotic arm, familiar to regular power wheelchair users. The buttons provide ways to store commands, specifically the stow and unstow functions. The stow function will automatically put the arm in a safe, preset position that will allow the user to safely power off the arm, and the unstow function would automatically move the arm to a “ready” position, a position that would allow the user to easily interact with their environment. Lastly, the displayed power switch will be used for natural startup of the system, while the switch on the power bank will be used during emergencies or if the primary switch fails.

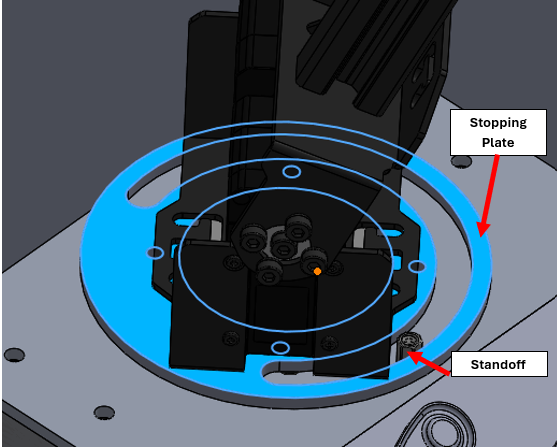
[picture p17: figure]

| Figure 4. Physical Stop CAD

One of the main concerns the team grappled with is how to physically limit the robotic arm’s range of motion to prevent unintended interactions between the robotic and the user. To remedy this problem, the system in figure 4 was developed. This system involves a small 3D-printed plate that attaches to the servo and rotates around the vertical axis along with the robotic arm. This plate provides a track that a standoff, attached to the top plate of the case, inserts into. While being small enough to avoid direct interactions with the arm, this standoff prevents the arm from moving too far by colliding with the 3D-printed plate, physically limiting the arm’s ROM (specifically to a 240-degree ROM about the vertical axis) and providing a safeguard for the user.

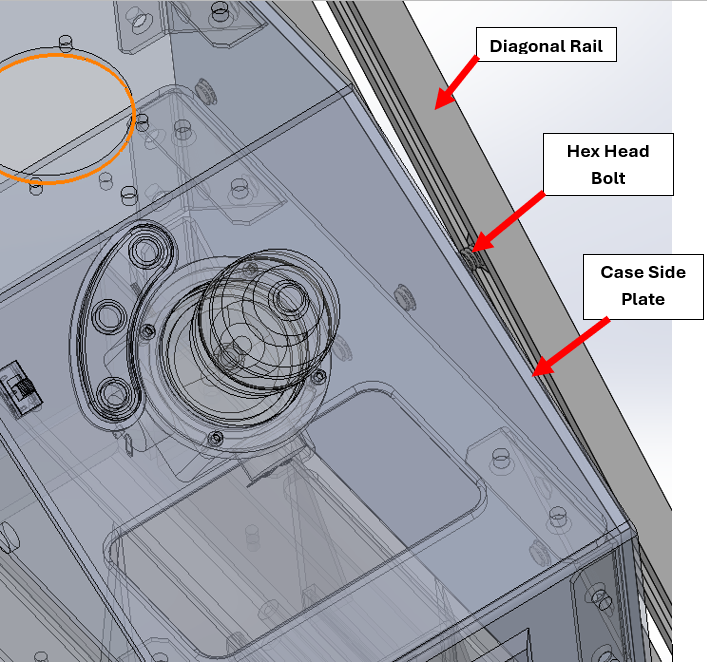
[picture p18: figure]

| Figure 5. Case to Mounting System Connection CAD

In previous designs, the case was big enough to reach the desired position where the user could reach the joystick comfortably. Subsequently, when the case’s dimensions were minimized, the case and robotic arm could no longer reach high enough to reach ADA standard elevator buttons. Furthermore, when vertical rails were added to allow vertical adjustment, the mounting system didn’t have enough space to provide sufficient stability. So, as seen in figures 5 and 6, diagonal rails (at a 45-degree angle) were added to allow the user to adjust the case to a height comfortable to them while also providing enough mounting space to the unitrack. Moving along inside these rails are ¼ inch-20 hex-head bolts that bolt to one side of the case, allowing the case to move with these bolts along the rail.

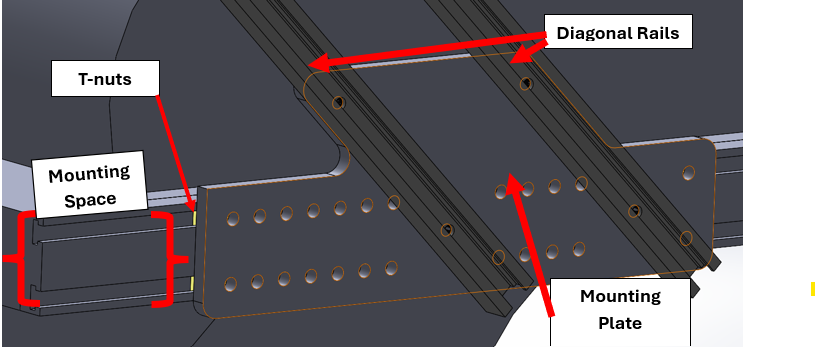
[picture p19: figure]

| Figure 6. Mounting System to Unitrack Connection CAD

The Unitrack, permanently bolted to the side of a Permobil wheelchair, allows for the mounting system to be attached via t-nuts as shown highlighted in yellow in figure 6. Connecting the t-nuts in the Unitrack to the diagonal rails is the mounting plate made of ¼’ thick aluminum, allowing multiple t-nut connections in the Unitrack to enhance stability.

# Status of Objectives and Requirements:

## System Level Objectives:

Requirements are defined using the format “TR A.B.C” where 1.X.0 indicates a system level requirement, and the X indicates the requirement number (1.1.0 indicates the first sys. level requirement, 1.2.0 indicates the second sys. level requirement, etc.). A green highlight means the objective is met, a yellow highlight means the objective is in progress, and a red highlight means the objective has not been met (failed). Table 1 highlights the four system level objectives for the project, which were determined through discussion with the end user and understanding the two high value functions for the system (use case).

Table 1. System Level Objectives

Technical Requirement ID | Requirement | Verification Method
TR 1.1.0 | The robot shall be controlled manually by a joystick and should have the ability to program automatic functions | Test
TR 1.2.0 | The robot shall have no more than six degrees of freedom | Inspection
TR 1.3.0 | The robot shall have an operating radius that spans a minimum of 5 inches to a maximum of 2 feet from mount location with 180 degrees of rotation total | Test
TR 1.4.0 | The robot and necessary electronics shall receive power from a rechargeable battery independent of the wheelchair electronics | Analysis

## Derived Requirements:

Similar to the system level objectives, the derived requirements follow the “TR A.B.C” format, where “A” corresponds to the system level requirement, “B” corresponds to the subsystem or derived requirement, and “C” corresponds to a secondary subsystem or requirement specifications. The first variable changes are based on the five main system level requirement categories. “TR 1.0.0” is the overall configuration, performance specification, and description. “TR 2.0.0” is the field use conditions and environmental effects mitigation. “TR 3.0.0” is the maintenance, installation, and service life. “TR 4.0.0” is the physical features and metrics. “TR 5.0.0” is the safety concern of the user and its surroundings. The “B” variable changes as it iterates from the corresponding category, defining the derived requirements for the category. Similarly, the “C” variable changes as it iterates from its corresponding derived requirement, providing additional specification or breaking the requirement up into more specific requirements. For example, “TR 1.1.0” is a one-time iteration requirement from "TR 1.0.0”, but “TR 1.1.4” is the fourth iteration of “TR 1.1.0”. Overall, the numbering nomenclature is useful in categorizing iterations of systems.

The majority of the derived requirements were developed through consultation with the team's customers. For example, TR 1.4.1 was developed through discussion with customers, who expressed the need for the system to last a full day (24 hours) before needing recharge since recharging the system requires the wheelchair to be stationary, which is not ideal for the customer. Requirements regarding size or shape specifications were determined by researching standards for wheelchair manufacturing, as well as standards for building entrances/exits and elevator door/button sizes and locations. TR 1.3.1 defines the overall height requirement the robotic arm must reach to depress elevator buttons and meet the primary objective for the end user. TR 1.3.1 was defined using ADA standards for button location and sizing in elevators [4], since these standards are in place to ensure that people such as our end users with DMD will have access to buildings and amenities that require the use of an elevator. Many of the requirements are currently in progress as the test plans have begun and will be completed in the spring, and some requirements necessitate prototype completion before updating their status to “met”. As of critical design review, no requirements have been “failed”.

Table 2. Derived Requirements

Technical Requirement ID | Requirement | Verification Method
TR 1.0.0 | The team shall research, design, develop, integrate, and test an assistive robotic device modified for a motorized wheelchair including a custom mounting device, electronics, and software | Customer Feedback
TR 1.1.0 | The robot shall be controlled manually by a joystick and should have the ability to program automatic functions | Test
TR 1.1.1 | The joystick shall be attached in a location near the motorized wheelchair armrest | Visual Inspection
TR 1.1.2 | Any automatic functions shall be independent of the joystick and should operate without any joystick inputs | System Test
TR 1.1.3 | The arm shall not mount in a location that infringes on the user's seating space, and must be small enough that as installed on wheelchair, the user can still pass through a standard door opening | Visual Inspection
TR 1.2.0 | The robot shall have no more than six degrees of freedom | Inspection
TR 1.3.0 | The robot shall have an operating radius that spans a minimum of 5 inches to a maximum of 2 feet from mount location with 180 degrees of rotation total | System Test
TR 1.3.1 | The device should be able to reach and depress elevator buttons and the handicap door button between 34 inches and 48 inches as specified by ADA standards | System Test
TR 1.3.2 | The system shall have an accuracy of + 10mm | Analysis, Test
TR 1.4.0 | The robot and necessary electronics shall receive power from a rechargeable battery independent of the wheelchair electronics | Inspection
TR 1.4.1 | The batter that powers the system shall last 24 hours between charged | Analysis
TR 1.4.2 | The battery shall remain installed in the case during recharge and should only be removed for maintenance or installation | Inspection
TR 2.0.0 | The robot shall operate in dry, arid conditions and should operate under rainy, humid conditions | Demonstration
TR 2.1.0 | The robot electronics shall be contained in a weather resistant enclosure | Inspection
TR 2.1.1 | The robot motors shall be secured in a weather resistant sleeve | Demonstration
TR 3.0.0 | The robot shall be installed in less than one hour and should be operational within thirty minutes of installation | Test
TR 3.1.1 | The robot shall be disassembled and reassembled for maintenance in less than three hours | Timed Test or PM/M Plan Development
TR 3.2.0 | The robot shall require maintenance every year and should be cleaned and inspected every 3 months | Analysis / PM/M Plan Development
TR 4.0.0 | The system shall be neutral in color and should blend into the motorized wheelchair structure | Visual Inspection
TR 4.1.0 | The system shall contain no sharp edges and should minimize sharp corners on frame, end effector, and joystick | Visual/Physical Inspection
TR 5.0.0 | The robot shall not cause harm to the operator in any way. | Inspection
TR 5.1.0 | Upon startup, the robot shall have safeguards against unexpected energization | Inspection
TR 5.2.0 | The robot shall have physical or program safeguards to prevent it from reaching undesired locations | Inspection
TR 5.3.0 | The robot shall have safeguards against unexpected de-energization | Inspection

# Critical Design:

## Engineering Analysis:

Structural Integrity (FEA)

To ensure the design's structural integrity and functionality, a free body diagram (FBD) was developed to model the physics acting on the system (figure 7). This analysis assumed the system would experience its maximum load conditions, with the arm fully extended and bearing the maximum anticipated strain. From the FBD, moment and force reactions were calculated and used to construct a Finite Element Analysis (FEA) model (figure 8). This FEA model represents the system’s case, with constraints applied at the connection points where the T-track links with the Unitrack.

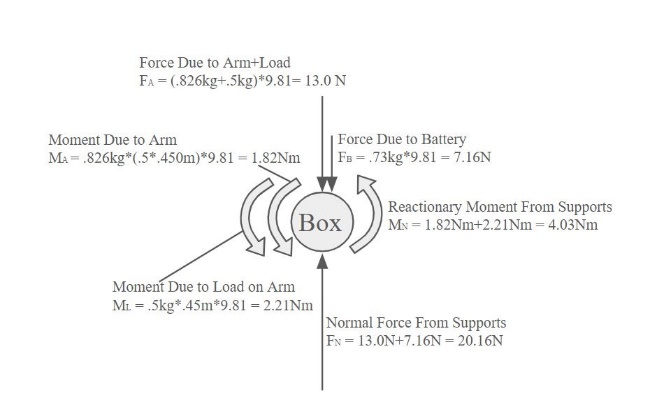
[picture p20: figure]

Figure 7. Free Body Diagram

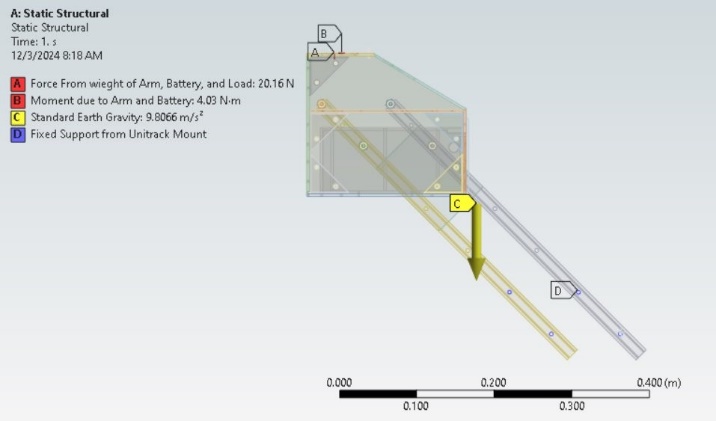
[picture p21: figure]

Figure 8. FEA Loads and Fixtures

Tests were conducted using Ansys to simulate the strain applied under maximum load conditions, incorporating forces derived from the FBD. Several iterations of the model were tested to ensure structural integrity, with updates made based on performance findings. The most recent modification included the addition of a welded plate along the T-track, which improved the factor of safety (FOS) by 0.6 and significantly reduced impulse deformation and vibration. Stress analysis revealed a peak stress of 48.436 MPa (figure 9), located at the T-track. When compared to the yield strength of anodized aluminum as shown in Appendix 1 this resulted in a FOS of 5.69. This high factor of safety confirms that the system can operate under maximum load conditions without the risk of material yielding, ensuring durability and reliability.

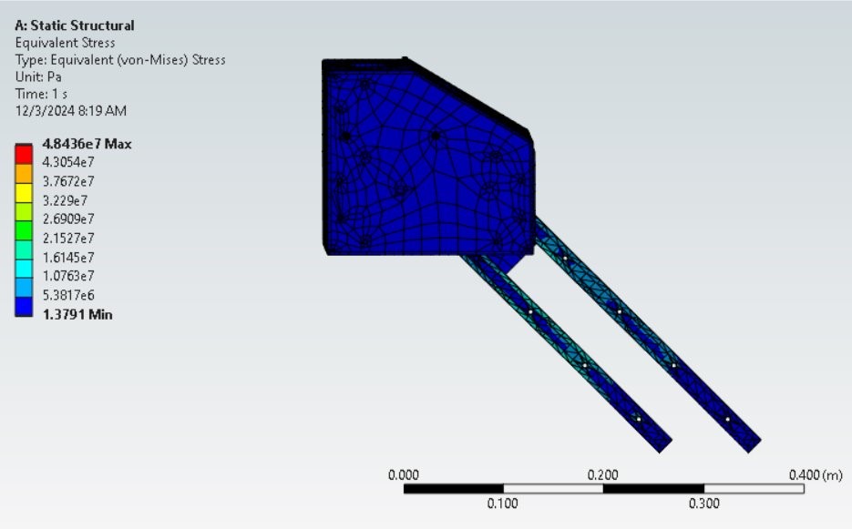
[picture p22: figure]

Figure 9. Finite Element Stress Analysis

Further analysis focused on deformation under maximum load (figure 10). Results showed a peak deformation of 1.62 mm, primarily concentrated in the T-track, which caused a slight downward shift in the system. Despite this, the inclusion of the welded plate limited the maximum tilt to 0.2 degrees—well within the acceptable parameters defined in the design requirements. These findings validate that the system performs optimally under extreme conditions, enabling progression to the construction phase.

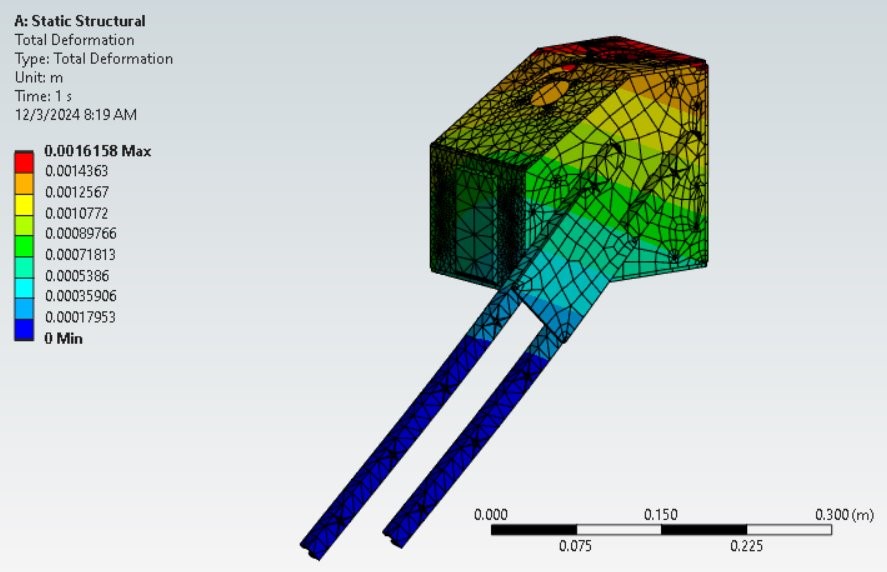
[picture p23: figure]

Figure 10. Finite Element Displacement Analysis

These results demonstrate the design’s structural integrity, confirming that it can withstand extreme operational conditions while maintaining the accuracy and performance standards necessary for its intended use.

End-Effector Accuracy

Team 205 has established a key accuracy requirement, defined as TR 1.3.2, stating that the system must achieve an accuracy of ±10 mm at full extension. This parameter ensures the system aligns with ADA minimum requirements outlined in chapter 4 section §407.4.6.2.1, which specifies that elevator buttons must have a minimum tolerance of ¾ inches (19 mm) [4]. Meeting this requirement is critical for ensuring the system’s usability in real-world scenarios. An analysis of the Waveshare was performed to determine its accuracy at the desired “full” extension; an extension of 17.72 inches. The primary factor impacting accuracy was identified as the compounding inaccuracies of the ST3215 servo motors controlling the arm's joints. These motors are advertised to have a resolution of 0.088° . Using this resolution an error was determined through calculating the step distance the end effector of the Waveshare arm can traverse at the desired maximum extension.

As three sets of servo motors are utilized to translate the final location of the end effector, the three error values are coupled to a final larger error value. The following equation provides the step resolution per motor depending on the length of the arm in question.

| Motor Accuracy=2∙length∙sin((0.088°)/2) | Eq. 1

As the servo motors attached to the base of the robotic arm will be subject to the full desired extension of the robotic arm through its rotation about the vertical axis and horizontal axis, the length value in the equation would simply be the full length of the arm, 17.72 inches. This creates an error value of about +/-0.0272 inches (+/-0.6909 mm) both horizontally and vertically along a wall plane at the maximum desired extension. This creates an error value of about +/-0.0272 inches (+/-0.6909 mm) both horizontally and vertically along a wall plane at the maximum desired extension. The third servo motor utilizes the same equation at a shorter length of 11.0295 inches (280.15 mm). The error value at this length comes out to a value of +/-0.0169 inches (0.4293 mm) vertically on the wall plane. Coupling the motor errors results in the horizontal error amounting to +/-0.0272 inches (+/-0.6909 mm) and the vertical error amounting to about +/-0.0441 inches (+/-1.1201 mm). Since these error values fall well under the minimum button size compliant with ADA standards (3/4 inch diameter), the system will be able to accomplish the high value function of pushing elevator call and destination buttons.

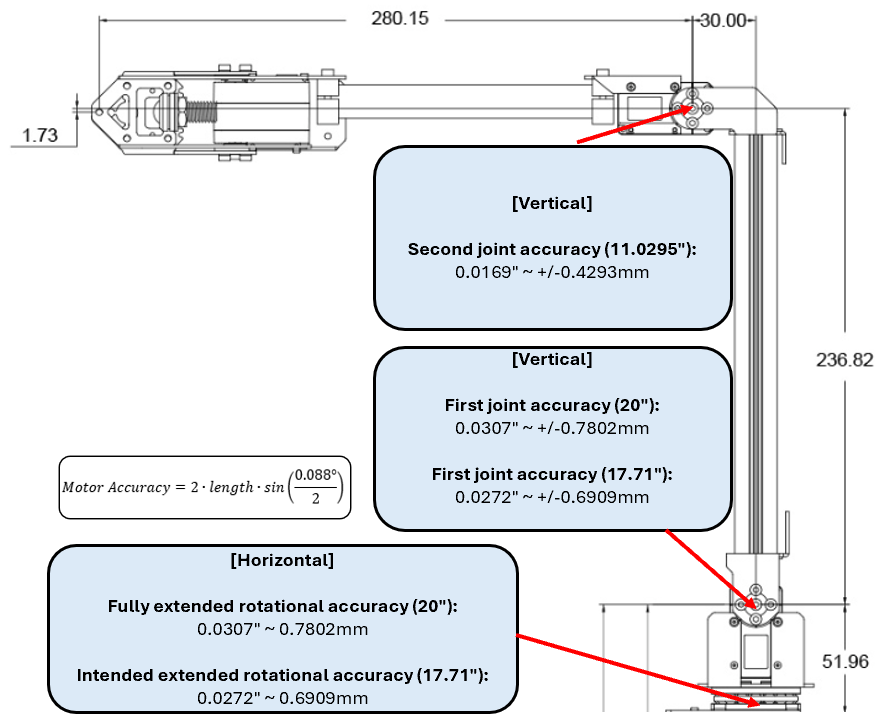
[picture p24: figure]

Figure 11. Diagram of Motor Accuracy

This analysis demonstrates that the system’s end-effector accuracy is sufficient to reliably interact with ADA-compliant elevator buttons and similar controls. These results, combined with physical testing to be conducted in later stages, validate the design's ability to meet user requirements for precise operation.

System Mapping & Dimensioning

The placement of team 205’s solution onto the Permobil M3 powered wheelchair is determined by the overall dimensions of the team solution, the Permobil M3 and specific guidelines set by ADA standards. The constraints fall below derived requirements TR 1.1.3 and TR 1.3.1.

Derived requirement TR 1.1.3 states that “The arm shall not mount in a location that infringes on the user's seating space and must be small enough that as installed on wheelchair, the user can still pass through a standard door opening”. This requirement constrains both the dimensions and positioning of the robotic solution. To determine the overall size of the team’s solution, measured values of the wheelchair were used and compared to the minimum door opening requirement set by ADA standards, which as outlined in chapter 4 section §404.2.3, states that a minimum clearance width of 32 inches is required for door openings [7]. In addition to the values measured from the Permobil M3, dimensions from the Permobil M3 user manual were also used [8]. The measured width of the Permobil M3 was found to be 24 inches at the base, 18 inches at the intended mounting location, and 28 inches at the armrest, giving the team a maximum profile of 9 inches to work within. Figure 12 provides a clearer understanding of how the dimensions were calculated.

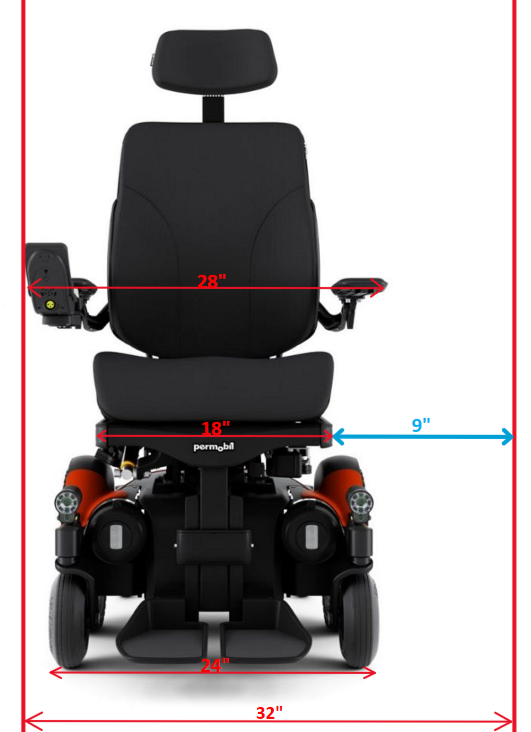
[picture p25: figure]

Figure 12. Maximum Profile width of system solution

Using this value the team worked towards decreasing the width to its minimum size using the largest inner component as a reference. This would be the width of the Waveshare robotic arm, which rounds to 3 inches [9]. The remaining inner components required for the system such as aluminum plates and corner brackets set the width of team 205’s casing solution at 5.25 inches. Once a prototype is fully assembled and mounted onto a Permobil M3, this requirement will be tested through visual inspection.

Derived requirement TR 1.3.1 states that, “The device should be able to reach and depress elevator buttons and the handicap door button between 34 inches and 48 inches as specified by ADA standards”. In order to fulfill this requirement, the following distances must be measured; the projected distance from the center point of the base of the Waveshare robotic arm to the wall, the Waveshare robotic arm’s maximum extended length, the height the system is off of the ground, and the heights to the lowest and highest push button determined by ADA standards outlined in chapter 4 section §407.4.6; 35 inches and 48 inches off of the ground [4]. As the Permobil M3 powered wheelchair is customizable to the user, there will be a few variable dimensions uncontrollable by the team. One such dimension is the length of the Permobil M3 armrest which affects how far or close the team's robotic solution would be from the elevator wall. The team created calculations to determine whether the end effector of the robotic arm would reach the wall at the maximum desired height of 48 inches and how far horizontally it can span the wall from one corner to the other at this maximum height. These calculations refer to the two extreme cases of a maximum and minimum armrest length of 18 inches and 13 inches respectively. Figures 13 and 14 demonstrate the dimensions used through measurements for the 18 inches armrest configuration.

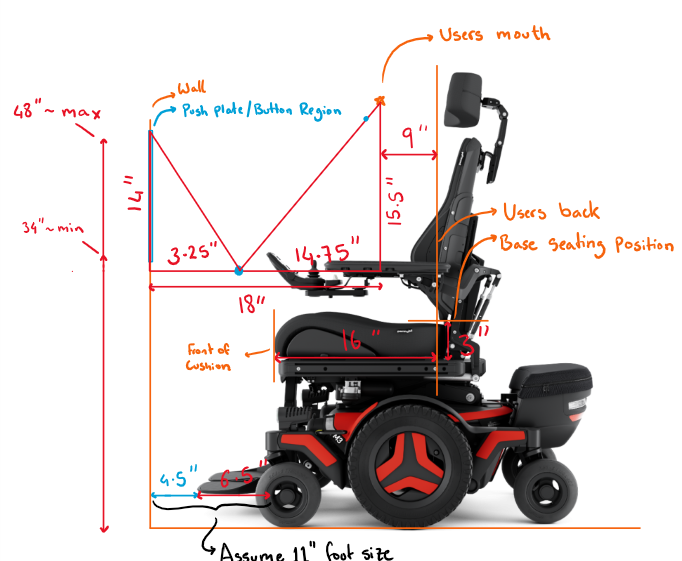
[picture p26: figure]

Figure 13. Measured Dimensions received on Permobil M3 (Side View)


Figure 14. Measured Dimensions received on Permobil M3 (Top View)

The 13-inch configuration and its respective calculations are shown in Appendix 2. Setting the maximum extendable length the robotic arm can reach to 17.72 inches ~ 450 mm, the Pythagorean theorem can be utilized to determine the corner-to-corner reach of the robotic solution (eq. 2).

| a^2 +b^2 =c^2 | Eq. 2

Viewing the system from the side view (figure 13) allows for the first unknown to be calculated, which is the diagonal distance from the furthest point on the elevator wall 48 inches from the ground to the robotic arms base location projected onto a leveled plane parallel to the ground surface.

| a^2 +14^2 =17.72^2 →√(17.72^2 -14^2)=10.86 in

Viewing the system from the top view (figure 14) allows for the second unknown to be calculated: the horizontal distance from one corner on the elevator wall at a height of 48 inches to the other corner at the same height opposite to the first.

| a^2 +3.25^2 =10.86^2 →√(10.86^2 -3.25^2)→10.37 in×2=20.74 in

These calculations demonstrate that the system can reach a maximum height of 48 inches from the ground as defined by chapter 4 section §407.4.6 of ADA standards and traverse a total distance of 20.74 in. The 13-inch armrest configuration also fulfills this requirement at a lower spannable distance of 10.4 inches.

Battery Requirements

Team 205 defined three battery requirements for the system, one of which is verified by analysis: TR 1.4.2 – the battery that powers the robot arm shall last 24 hours between charges. This requirement will be met depending on the team's selected battery. The battery size can be determined based off the power consumption of the robotic arm, the most power-hungry component of the system. For simplifying assumptions, the team assumes that all movements of the robotic arm will pull 5A (I = 5A), and anytime the robot is not moving it will pull 0.2 A (I_min = 0.2A). The system has two objectives: pushing an elevator button and bringing a drink to the user's face. The team assumes that pushing an elevator button occurs 30 times a day (freq_b = 30) and takes 15 seconds to complete the task with the system (time_b = 30 s). Furthermore, the team will assume that bringing a drink to the user's face occurs 30 times a day (freq_w = 30) and takes 20 seconds to complete the task (time_w = 20s). The time at max output is the sum of total time spent pushing an elevator button and bringing a drink to the user (eq.3). Then, the time at minimum output is 24 hours minus the time at max output (eq.4). The time at max output is multiplied by the max current, and the time at minimum output is multiplied by the minimum current, and these two values are summed to determine the battery size and output (mAh) (eq.5).

time_max= ((freq_b *time_b )+(frew_w *time_w ))/((3600))= 0.2917 hours | Eq. 3
time_min=24-time_max=23.7 hours | Eq. 4
req_(mAh) =((I*time_max)+(I_min *time_min⁡))*1000=6200 mAh | Eq. 5

The current electronics in the system will require a 6200 mAh 12V battery to be able to complete both objectives 24 hours before a recharge. Though the analysis shows only a 6200 mAh 12V battery is needed, team 205 chose a battery larger than this to account for differences in frequencies of events from person to person, as well as possible differences in loading on the arm or paths the arm takes. The team chose the “Talentcell 12V Lithium Ion Battery” [10] seen in figure 15, which is rechargeable and can deliver 38400 mAh to the system, meeting TR 1.4.2 and overshooting the requirement value for any unplanned uses of the arm. The code used to calculate the battery requirement can be found in Appendix 3.


Output to robotic arm

Charging Port

Figure 15. Talentcell Power Bank [10] (https://www.amazon.com/TalentCell-PB120B1-Rechargeable-38400mAh-142-08Wh/dp/B07H8F5HYJ)

## Preliminary Test Plan:

Preliminary test plans have been developed for requirements with “by test” as the verification method. Test plans will be reviewed and refined in the spring for clearer instructions and better data acquisition. The test will be completed as the necessary subsystem is completed and equipment is available. The system is subject to reverification after extended use or modifications that directly or indirectly affect the tested subsystem. Availability is not a primary concern as the required tools are easy to access. Preliminary test plans are summarized in table 3 shown below:

Table 3. Preliminary Test Plans Descriptions

Requirement | Description | Test Description | Equipment | Expected Outcome
1.1.0 1.3.0 | 1.1.0 The robot shall be controlled manually by a joystick and should have the ability to program automatic functions accessed through a button push 1.3.0 The robot shall have an operating radius that spans a minimum of 5 inches to a maximum of 2 feet from mount location with 180 degrees of rotation total | Move the joystick through all ranges of control to extend the robot the maximum distance in every direction. Record the distance from the base of the arm to the tip of the end effector For automatic functions, run each function and ensure correct movement by comparing the position response to the command sent | Waveshare Robotic arm Tape Measure Joystick Computer | Expect the distance recorded by the tape measure to not exceed programmed limit Expect coordinates of automatic functions to correspond to the position feedback of the robotic arm 1.3.0 will be verified as the arm will pass through all octants during the test
1.3.2 | The system shall have an accuracy of ±10mm to ensure accuracy over extended use | An arbitrary point will be picked, location marked, and coordinates recorded. The arm will be moved away and moved back to this location through a set of JSON commands, and the offset will be recorded | Waveshare Robotic Arm Dial Caliper Computer Sharpie/Pen USB A to C cable | Expected offset <10mm (.3937 in) and coordinates that match the original point. Expected that the arm will pass test according to theoretical analysis
3.0.0 3.1.1 | 3.0.0 The robot shall be installed in less than one hour and should be operational within thirty minutes of installation 3.1.1 The robot shall be disassembled and reassembled for maintenance in less than three hours | Record time of installation, time till operation, time of uninstallation. Reading instructions provided by the team are included in the time. Three separate times recorded | Complete system (robot arm, joystick, battery, other electronics, hardware, mount) Stopwatch Screwdriver/Drill | Expected install and uninstall time of 45 minutes. Expected time till operation of 15 minutes. If recorded times are less than limits, requirement is met

# Bill of Materials:

Key items to system composition/construction can be found in table 4 shown below. A full list of the bill of materials can be found in Appendix 4 along with additional construction hardware. Items that have been purchased include the robotic arm, the 4-axis joystick, the 12V battery, and the Permobil Unitrack. Items that have been received include the robotic arm, Unitrack, and the 4-axis joystick.

Table 4. Bill of Materials

Item | Description/Use | Vendor | Quantity | Price Per Unit | Total Price (T & S/H)
Waveshare RoArm-M2-S Robotic Arm SKU:25118 | Robotic arm to be mounted to wheelchair | Waveshare (https://www.waveshare.com/product/robotics/robot-arm-control/robot-arm/roarm-m2-s.htm?sku=25118) | 1 | $ 189.99 | $229.59
4 – Axis Joystick JH-D400X-R4 | Controller for robotic arm | Amazon (https://www.amazon.com/SaiDian-4-Axis-Joystick-Potentiometer-JH-D400X-R4/dp/B08CGYGMJL) | 1 | $17.89 | $17.89
Talentcell 12V Lithium Ion Battery PB120B1 | Power source for robotic arm (12V 38400mAh) | Talentcell (Amazon) (https://www.amazon.com/TalentCell-PB120B1-Rechargeable-38400mAh-142-08Wh/dp/B07H8F5HYJ?mcid=4d9721f459d23e829a73bdaec0a33bbe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) | 1 | $91.09 | $95.54
Permobil Unitrack SKU: 321440 | Mounting location for system for fitment testing | Build My Wheelchair (https://buildmywheelchair.com/unitrack-bar-17-18-19-seat-depth-corpus-3g-vs/) | 1 | $48.00 | $62.99
18” T-Track Fixturing Track 1850A11 | Vertical tracks for system adjustments | McMaster (https://www.mcmaster.com/1850A11/) | 2 | $9.83 | $19.66
Rubber Gasket 3/32” 20’ length | Gasket for lining exposed edges for waterproofing | Protalwell (Amazon) (https://www.amazon.com/Rubber-Channel-Protector-Length-Shaped/dp/B0BN3HZKY1?mcid=9bcbbe47a7b634ab949f484885b9e626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) | 1 | $15.99 | $16.84
1/4” 6061 Aluminum Sheet 1x1ft P314T6 | Raw Material for case and mount construction | Metals Depot (https://www.metalsdepot.com/aluminum-products/6061-aluminum-sheet-plate) | 1 | $48.88 | $48.88
1/8” 6061 Aluminum Sheet 1x1ft S318T6 | Raw Material for case and mount construction | Metals Depot (https://www.metalsdepot.com/aluminum-products/6061-aluminum-sheet-plate) | 3 | $49.98 | $149.94
Corner Reinforcing Brackets | Raw Material for case and mount construction | McMaster (https://www.mcmaster.com/1088A31/) | 10 | $3.92 | $39.2

# Project Management:

## Risk Summary:

The risks for the project are broken into three categories: technical performance, schedule or milestone, and cost. Technical risks make up the majority of current risk and thus have been further broken down into four subsections for organization: Physical risks, electrical hazards, program risks, and safety risks. Note: Although electrical hazards are considered a physical risk, it is separated for the purposes of organization and clarity.

Table 5. Table of Risks

Likelihood | 5 | 0 | 0 | 0 | 0 | 0
| 4 | 0 | 0 | 0 | 0 | 0
| 3 | 0 | 0 | 0 | 0 | 0
| 2 | 1 | 3 | 1 | 0 | 0
| 1 | 1 | 4 | 0 | 0 | 0
| | 1 | 2 | 3 | 4 | 5
| | Severity

Technical Risks: The first technical risk is the shearing of bolts, welds, and tracks used for mounting the Waveshare which is greatly dependent on the mounting position and magnitude of externally applied loads. Another similar risk is the buckling/bending of robotic arm members due to excessive loads or improper use. This is greatly dependent on robotic arm choice regarding the structural material of linkages. Water damage is also considered a technical risk since it can be mitigated by the enclosure for sensitive components such as servos, microcontrollers, and power banks.

Electrical Hazards: The first electrical hazard is the overheating of electrical components, which may cause technical/ electrical failure and deformation of parts. Next, it is possible that power surges through the system when the battery is first connected which could cause damage to other electronics and cause a potential fire hazard.

Programming Risks: The first programming risk is if a programmed function exceeds its expected operating time (gets stuck in a loop) such as moving a water bottle between two points indefinitely. The second programming risk is if a delay between the robotic arm and joystick causes inaccuracy in performing functions.

Safety Risks: The main safety risk of concern is the arm exceeding its allowed range of operation which is determined by user proximity.

Scheduling Risks: Since the team will make use of the machines and welding equipment in the applied lab, it is necessary to evaluate the risk that arises from scheduling as many other teams will also need to use this equipment.

## Risk Mitigation:

Technical Risks: The robot mount location greatly affects the distribution of weight, stress, and strain. To address this risk, an FEA was used to analyze the mount at its most optimal position on the wheelchair, in which a stress/strain analysis was performed on the robotic case, horizontal, and vertical tracks (with truss). However, an analysis was not performed for the McMaster bolts as these are able to withstand loads that exceed the scope of the project. Similarly, the choice of the Waveshare robotic arm mitigates the risk of buckling/bending members due to its structural material of carbon fiber and 5052 aluminum alloy, both of which are known for their mechanical strength. Water damage will be mitigated by enclosing the power bank, wires, and ESP32 in an aluminum case lined with welds and rubber gaskets. The casing of the Waveshare’s exposed servos and wires is still under consideration since previous solutions such as a heat shrink were suggested to be an insufficient choice after an extended period. With exception to this, the current design mitigates all of the technical risks according to engineering analysis methods, but further testing will be conducted in the spring once building begins.

Electrical Hazards: The concern of overheating is mitigated through material choice of the robotic case and application of proper ventilation. More specifically, the robotic case is to be composed of 6061 aluminum plates which have a high thermal conductivity [6]. Also, the robotic case design includes ventilation holes along one side to allow for cooler air to enter. Lastly, to ensure no power surges, the team will include a breaker (switch) between the battery and the rest of the system to mitigate any effects which will be included during spring manufacturing.

Programming Risks: To mitigate the risk of functions exceeding operational time, a pre-programmed time limit will be set to compare active operating time such that it ends all operation if the active operating time exceeds the time limit. Secondly, the risk of joystick delays causing inaccuracies will be mitigated by configuring sensitivity of the joystick to account for any delay. Currently, the programming risks have not yet been mitigated since only starter code has been implemented, thus, the software is not ready for the integration of these pre-programmed features.

Safety Risks: This high severity risk will be mitigated through the use of mechanical and programmed stops and limiters. Currently within the design, a physical stopper is set to limit the 360° motion at the base using a guided slot and standoff. Similarly, the programmed stops/ limiters will limit the 180° motions at the shoulder and elbow joints. Although only the mechanical method has undergone analysis, both methods still require testing which will be conducted in the spring.

Scheduling Risks: To prepare for possible spring scheduling conflicts, the team will prepare fully dimensioned engineering drawings over break with a list of possible machines used so that Matt can review the drawings and suggested manufacturing plan and advise/coordinate with the team for scheduling the manufacturing and assembly of our system.

## Schedule:

Within the spring semester, the team will first gather all necessary hardware and construction material such as 6061 aluminum plates, brackets, rubber gaskets, etc. for the robotic case. Ideally, the team will consult Prof. Moyer and receive approval for these materials prior to winter break so that they’re available at the beginning of spring semester. Otherwise, the team will continue with other unconstrained tasks until these materials have been received. These other tasks will include scheduling training and manufacturing time in the Ware Lab and modifying the Jazzy wheelchair. Once the construction materials have been received, the team will then machine and weld all necessary parts during a reserved timeslot. With these parts fully machined, the team may then line exposed edges with rubber gaskets and bolt on the remaining plates after integrating the internal components: Waveshare robotic arm, joystick, power bank, and wiring. The integration of internal components will likely be delayed until the system software is sufficient, so while some members focus on manufacturing the case, others will focus on developing code for the system. As seen in the Gantt Chart, the robotic case will be fully assembled by Test Readiness Review (TRR) during the first week of March. Shortly after spring break, the team would like to visit a member from our sponsor so that we may test our physical system on their wheelchair and receive real time feedback, from which the team will refine the design based off feedback and suggestions from the end user.

Additionally, the team will modify the Jazzy wheelchair to replicate the mounting schematic of a Permobil wheelchair. This will entail adding mounting points on the Jazzy such that a Unitrack may be attached for the robotic case mount. These mounting points will be fabricated through spare parts taken from the Hoveround wheelchair. This task will be completed by the end of January which allows ample time until the completion of the robotic case.

Throughout the semester, the team will program the interface between the Waveshare and joystick. This task will take place throughout the entire spring semester since both objectives and automated functions depend on the software interface. More specifically, the first objective of manually pushing an elevator door/ handicap button with the Waveshare and automating stowing/ unstowing, would ideally be completed by the end March. If this timeline is concrete, the team would then begin work on the second objective which is bringing a cup to the user’s face, all of which must be completed by the end of April in time for the Spring Final Review and Capstone Expo.


Figure 16. Spring Semester Gantt Chart

## Budget:

The team has been allocated a maximum budget of $5,000 and the team is solely responsible for allocating expenses for parts and materials while also maintaining emergency funds.

As shown in Figure 17, a visualized budget expenditure is used to track the budget over the following months. Currently, only the Waveshare, joystick, Unitrack, and power bank have been purchased in November with a total cost of $406.01. Notably, since December embodies most of winter break, there are no expected purchases during this period. As previously mentioned, the hardware and construction materials will be ordered upon approval, though the total expected cost of $416.74 has been allocated to January. As the project progresses in the spring semester, the team will likely need to order additional materials or replace parts due to damage caused by prototyping and testing. For this, at least $200 has been allocated for each month of February, March, and April. With this in place, the team has a remaining budget of approximately $3,500 which is well under budget.


Figure 27. Budget Summary Graph

# Conclusions and Future Work:

Following a finalized design and analysis, the team is currently on track to performing the high value function of pushing an elevator button. Analysis has shown that the current components chosen for system composition will be able to operate under normal conditions and meet the requirements of the end user. Though the team has a solution for waterproofing the robotic arm, suggestions from reviewers and other engineers push the team to look for a different solution as the current material chosen may have long term issues after extended use. Mathematic analysis of the current design shows that the system will be able to reach all elevator buttons complaint with ADA standards and can structurally support all loads under the ideal use case, with room for potential unexpected load to be supported (if the system is bumped or hit). Additionally, the team is $3500 under budget, so if the currently chosen robotic arm does not meet end user requirements, the team have the capabilities of purchasing a different robotic arm and testing it on our system.

Once the team returns from winter break, construction of the case and mount, and testing of the electronics and code will begin. At first, the team will 3D print the case to prototype mounting and stress points to adjust the design. Later, the team will schedule time with Matt Collins in the APPLIED lab to machine the plates that make up the case, drill mounting holes, and wire paths into this case. Additionally, the team will schedule time to weld the plates together to form the case, and test if the electrical components fit inside the case to ensure proper manufacturing. While the team constructs the case and mount, testing of the robotic arm and joystick will also be completed. Since the joystick has been acquired, the team can work on coding in the joystick controls to the robotic arm and test the features the team will include in the final prototype. Lastly, the team will modify the jazzy wheelchair acquired to represent the dimensions of the Permobil M3 Corpus, since the M3 is one of the most common wheelchairs used by people with DMD. The modified jazzy will be used for fitment testing of the system and presentation purposes in the spring.

# References:

[1] “About Duchenne” (2020), Parent Project Muscular Dystrophy. https://www.parentprojectmd.org/about-duchenne/ (Accessed Dec. 10, 2024).

[2] Strachan, S.,2024. “Adaptive solutions: Assistive technologies for DMD”. Muscular Dystrophy News Today. https://musculardystrophynews.com/assistive-technology-for-duchenne-muscular-dystrophy/ (Accessed Dec. 10, 2024).

[3] “Robotic Arm” (n.d), Kinova Inc. https://assistive.kinovarobotics.com/product/jaco-robotic-arm (Accessed Dec 10, 2024).

[4] “Guide to ADA Accessibility Standards” (n.d), U.S. Access Board. https://www.access-board.gov/ada/guides/chapter-4-elevators-and-platform-lifts/ (Accessed Dec. 10, 2024).

[5] “Permobil Unitrack frame,” Mount’n Mover. https://www.mountnmover.com/support/wheelchair-mounting/permobil-track. (Accessed Dec. 10, 2024).

[6] Zhang, A., Li, Y., 2023. “Thermal Conductivity of Aluminum Alloys – A review”. National Library of Medicine, PubMed Central., https://doi.org/10.3390/ma16082972 (Accessed Dec. 10, 2024).

[7] “Guide to ADA Accessibility Standards 404.2.3 Clear Width” (n.d). U.S. Access Board. https://www.access-board.gov/ada/#ada-404_2_3 (Accessed Dec.10, 2024).

[8] “M3 Corpus Model 2 User Manual” (n.d). Permobil. https://permobilwebcdn.azureedge.net/media/vkgi5yyd/m3_corpus_model_version_2-user_manual-eng-us-337261.pdf (Accessed Dec 10. 2024).

[9] “RoArm-M2 Desktop Robotic Arm Kit”. Waveshare. https://www.waveshare.com/roarm-m2-s.htm (Accessed Dec. 10, 2024)..

[10] “Talentcall 12V Lithium Ion Battery PD120B1”. Talentcell. http://talentcell.com/lithium-ion-battery/12v/pb120b1.html (Accessed Dec. 10, 2024)

# Appendices:

Appendix 1: Anodized aluminum data sheet


Appendix 2: Configurations and Calculations


Appendix 3: Code used to calculate the battery requirement


Appendix 4: Bill of Materials


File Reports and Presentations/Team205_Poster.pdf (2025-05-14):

# Team 205: Robotic Arm to Assist Motorized Chair Users

### Sponsor: Mr. Keith Van Houten, PPMD Team Members: Brooke Harrington, Justin Lee, Cavan Moriarty, Omar Abuljobain, Andrew Baum Faculty Advisors: Mr. Stephen Moyer, Mr. Jim Hess

Duchenne muscular dystrophy (DMD) is a progressive disorder that deteriorates muscles over time.
- Users with DMD often require the use of motorized wheelchairs (Permobil M3)
- People with DMD have limited range of motion (ROM) and often require a caretaker or robotic device to help with everyday tasks
Waterproofing | Waveshare Ro-Arm

### Complete Two High Value Functions

### Push an ADA compliant elevator button

### Retrieve and return a drink to and from the user from a user programmed location

# Background

# Mounting


# Conclusions

# Problem Statement

# Customer Needs

Current assistive devices are too expensive, cover a large footprint, and are difficult for people with DMD to control.
People with DMD would benefit from a simple to control, affordable robotic aid that executes specific high value functions.

### - Possible better robot arm choices – more research - Refined case design - Reworked electronics: different microcontroller and printable circuit board instead of protoboard

### ✓ Completes high value functions and meets

### user requirements

### ✓ Affordable at < $2,000

### ✓ Compatible mounting with Permobil wheelchair

### ✓ Open source – GitHub

### The Werth Family and the Team at PPMD

Mr. Jim Hess,
Mr. Stephen Moyer,

### Mr. Rick and Ms. Kristie from QL+

## Recommendations

&

## What we’d do differently

# Team Testing

Test | Results / Outcome
End Effector Load Capacity | ✓ 0.5 kg at max distance ✓ 0.6 kg at min distance
Verification of Safety Measures | ✓ Stayed within designated 300° of rotation
Joystick-Robot Accuracy | X Failed team standards ✓ Met ADA standards
Installation Time | ✓ 58.52 sec
Maintenance Time | ✓ 22 min 5 sec

# End User Testing

# Protoboard

- 1 joystick (3 axis, 2
buttons)
- 2 switches for system
& joystick enable
- 5 buttons for stored
functions/location

Team 205 meeting with
Colin Werth for testing

# Special Thanks!

# Images

Mounting Assembly
Features:
- Locking pin
- Vertical and
horizontal
adjustment
- Easy tightening
- French cleat
system

# GitHub

End User Comments:

- Move the joystick closer to the edge to be in line
with the armrest
- Joystick with twisting
motion may not be ideal
for people with DMD
- End-effector tip requires non-slip material for
button pressing
- Armrest attachment for
additional support
- End-effector cover protects wrist servo
- Sleeve protects elbow and base servo
- Well protects internal electronics
Safety – Robot doesn’t hit user or other people | System withstands rainfall whilst maintaining normal operation
Ease of assembly, installation, and maintenance | Easily portable and self-contained for travel
Intuitive Controls that are like controls found on the wheelchair | Attached system fits through ADA compliant doorframe
Affordability (current market solutions >$60,000) | Ability to save custom, frequently-visited locations using buttons

### Colin testing: - Mounting position - User interface - Retrieving a drink - Ergonomics - Fitting through an ADA compliant door

### Team testing: - Accuracy of robot to hit elevator button - End effector slipping - Visibility, ease of maneuverability

GitHub Information
- Code
- CAD Files
- Tutorials
For others to reproduce
our project and expand
upon our work

# Control Panel

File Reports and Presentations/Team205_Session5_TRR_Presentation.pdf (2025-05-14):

# TEAM 205 – ROBOTIC ARM TO ASSIST MOTORIZED CHAIR USERS

Industry Sponsor: PPMD, Mr. Keith Van Houten

Faculty Advisor: Prof. Jim Hess

Team Members: Brooke Harrington, Cavan Moriarty, Omar Abuljobain, Justin Lee, and Andrew Baum

# Agenda

Background & Recap; • Objective and Solution Overview; Solution Summary; • High Fidelity CAD • Key/ Important Features • Design Changes; Build Progress; • Mounting Schematic • Electronic Casing • Software Functions; Test Readiness; • Key Requirements • Test Methods; Project Management; • Timeline and Budget

# Duchenne Muscular Dystrophy (DMD)


Background | Solution Summary | Build Progress | Test Readiness | Project Management

Users with DMD often require the use of motorized
wheelchairs (Permobil M3)
and aid from caretakers or assistive devices

Current assistive devices such as the Kinova JACO are:
- Expensive (>$60,000)
- Difficult (https://assistive.kinovarobotics.com/product/jaco-robotic-arm) to control
- Large/Bulky
- Difficult to remove from wheelchair

Figure 1: (https://assistive.kinovarobotics.com/product/jaco-robotic-arm) Kinova JACO mounted on Permobil wheelchair

DMD is a progressive disorder that deteriorates muscles over time
- 1 in 5000 boys affected yearly

Fi (https://assistive.kinovarobotics.com/product/jaco-robotic-arm)gure 1: Kinova (https://assistive.kinovarobotics.com/product/jaco-robotic-arm) JACO mounted on Permobil wheelchair

Current assistive devices such as the Kinova JACO are:
- Expensive (>$60,000)
- Difficult to control
- Large/Bulky
- Difficult to remove from wheelchair

DMD is a progressive
disorder that deteriorates muscles over time
- 1 in 5000 boys affected
yearly

Users with DMD often
require the use of
motorized wheelchairs
(Permobil M3) and aid
from caretakers or
assistive devices

Figure 2: (https://assistive.kinovarobotics.com/product/jaco-robotic-arm) Kinova JACO robotic arm

# Key Objectives


Modify a low-cost robotic arm and design mounting structure to attach

to common motorized wheelchairs (utilizing Permobil Unitrack); Complete Two High Value Functions; Push an ADA complaint elevator button; Retrieve and bring a drink to the user from a user programmed location, then return the drink to this location

# Summary of Changes Since CDR

Current
- Structure:
- 3D Printed Frame
- Integrated Middle Plate
- Nut-Inserts
- Mounting:
- French Cleat Mounting
Assembly
- Electronics:
- ESP32
- Protoboard
- Header Pins
- Adafruit Feather v2
- Buttons and Switches
- Material:
- Acrylic Plates
- Waterproofing:
- Boot
- Sleeve
- 3D printed Ring


CDR
- Structure:
- Corner Brackets
- Mounted Middle
Plate
- Mounting:
- Rigid Mounting to
Rails
- Electronics:
- ESP32
- Material:
- Aluminum
- 3D Printed Plates
- Waterproofing:
- Heat Shrink

# Since CDR – Structure

CDR; Current 3D Printed Frame; Nut-Inserts; Space for Protoboard; Holes for Power Cable

Change:
• Corner Brackets to 3D Printed
Frame
• Nuts and bolts to Nut-Inserts
• Middle plate integrated

Reason:
• Assembly/disassembly time
reduction
• Maintenance access
• French Cleat installation access
• Protoboard installation access

Impact:
• Significant reduction in
installation time
• Simplifies installation process
• Delay due to 30-hour print time

Button Head Bolt

# Since CDR – Mounting System


CDR

Hex Head
Bolts

Pin Slot

T-Slot
Rails

French Cleats
(lower)

1/8”
Aluminum
Plate

Side Plate
of Case

3D Printed
Pin

French Cleats
(upper)

Current

Change:
- Rigid Mounting of Case Side Plate to French Cleat Mounting System
- 1/8” Aluminum Mounting Plate
- 3D Printed Pin
Reason:
- Sponsor Team Requirement to be able to move case quickly and easily.
- Pin prevents case from being bumped off
Impact:
- Significant reduction in installation time
- Simplifies installation process
- Increases transportability
- Delay due to booked Plasma Cutter

Side Plate
of Case

Hex Head
Bolts

T-Slot Rails

# Since CDR – Electronics

CDR; 4-Axis Joystick; Arbitrary Buttons; Arbitrary Switch; ESP32; Pin Headers; Protoboard; Adafruit; Feather v2; Switches; Buttons; LED; Change:; Current; • Added Adafruit Feather v2 • Added protoboard with pin headers • Added Switches • Added Buttons • Added LEDs • Removed Arbitrary Buttons and Switch Reason: • Can’t exclusively use ESP32, feather allows for analog communication; and sturdy connections • Switch and buttons added per sponsor team request Impact:; • Delay due to reprint of frame to fit protoboard; and LEDs

- Protoboard and pin headers allow for easy
- Much easier to understand user interface
- Delay laser cutting diagonal plate due to multiple changes to fit buttons, switches,

# Since CDR – Waterproofing


3D Printed Ring
to Protect the
Top of the Case

Press Fitted Battery
Cover to Protect
Inner Chamber

Water resistant
Boot

Water
Resistant
Sleeve

Heat Shrink to Cover
Exposed Joints

CDR

Current
Change:
- Heat Shrink to Leather Boot and Sleeve
- Added Battery Cover
- Added 3D Printed Ring
Reason:
- Heat Shrink wasn’t durable or malleable enough
- Waterproof boot allows for 360-degree base rotation
- Waterproof sleeve is malleable enough to allow 180-degree servo rotation
- Battery needed a cover to prevent water damage
- Easy installation and application Impact:
- Entire robot arm and its electronics becomes waterproof
- Amazon order was lost, causing delay
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

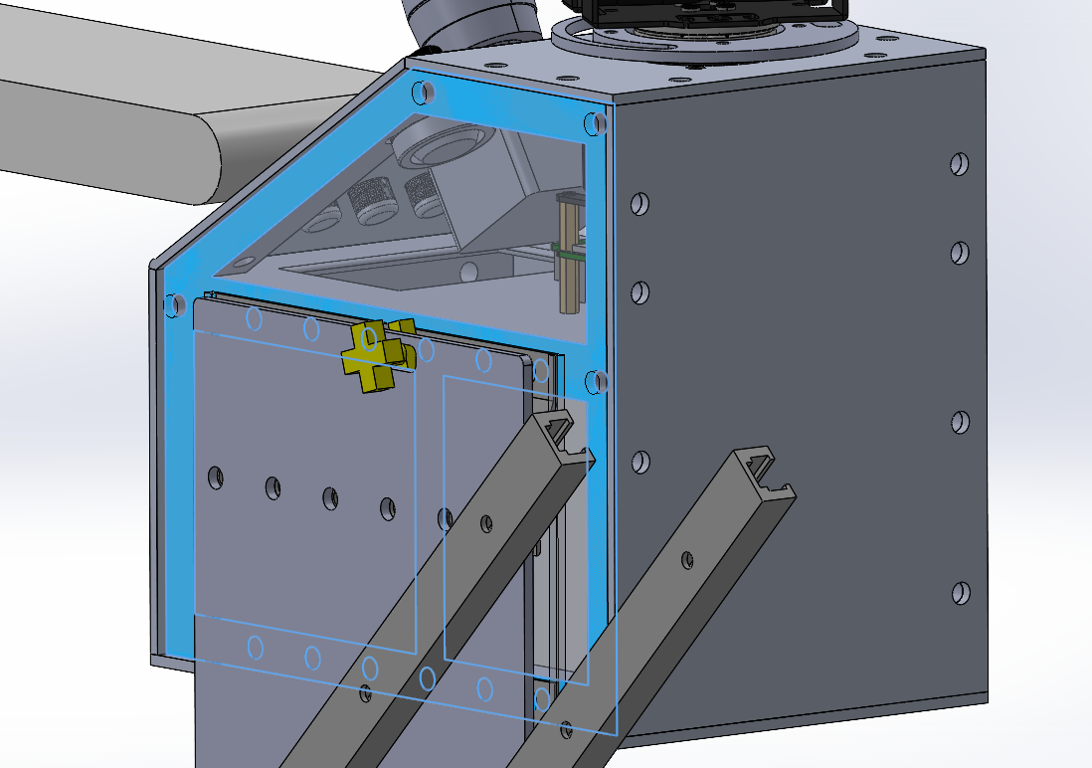
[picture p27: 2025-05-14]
CADFiles&Drawings/DXF and PDF Files/Reference Images/ConnectingFramePlateView2.png

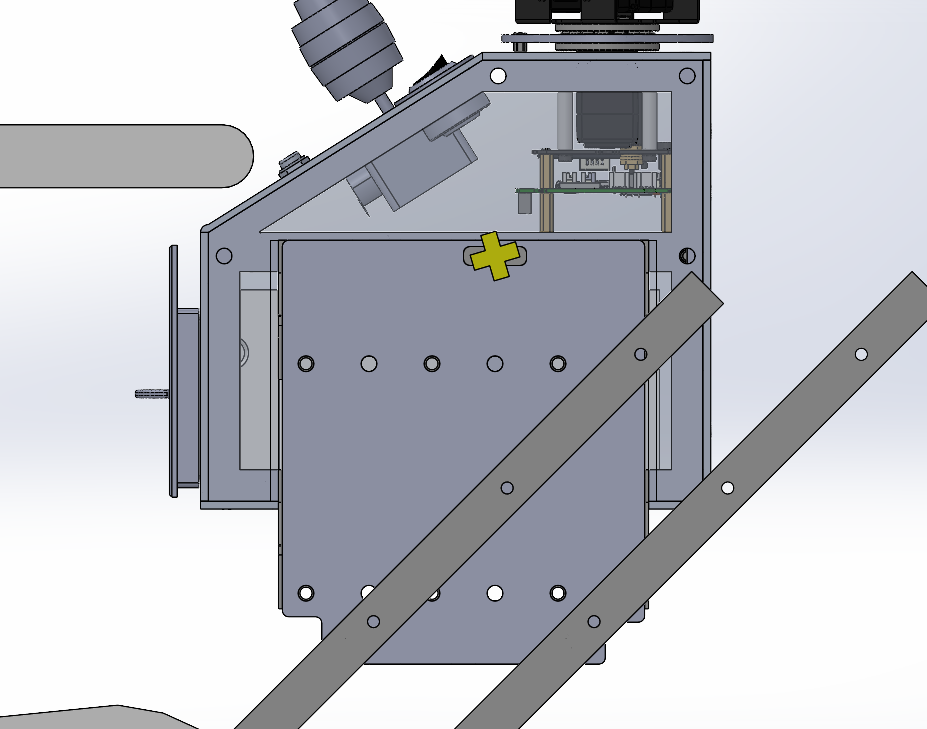
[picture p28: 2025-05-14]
CADFiles&Drawings/DXF and PDF Files/Reference Images/ConnectingFramePlateView1.png

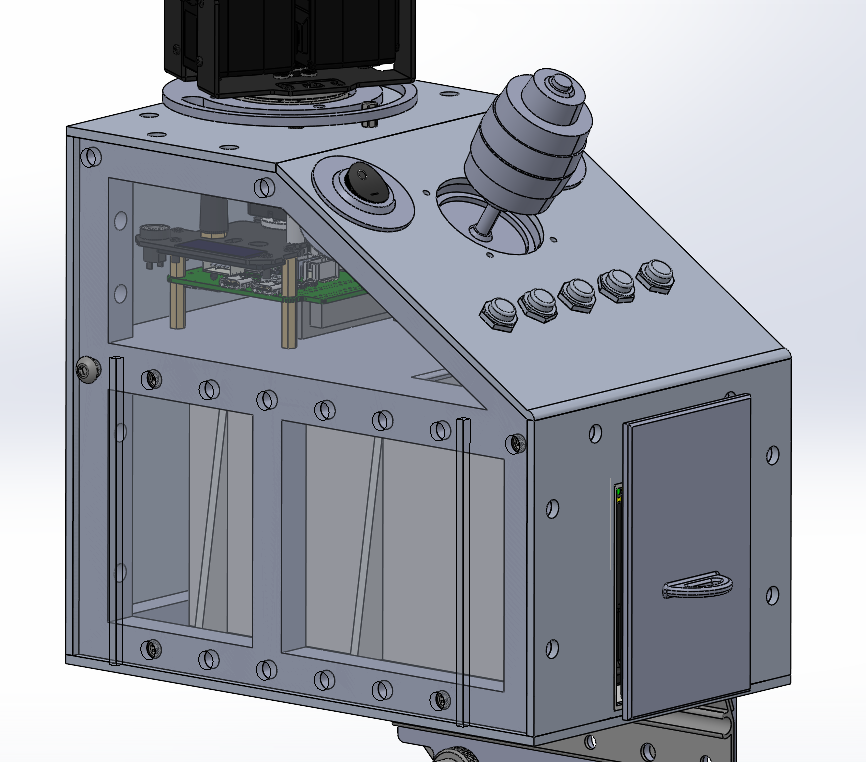
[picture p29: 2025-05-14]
CADFiles&Drawings/DXF and PDF Files/Reference Images/CaseView1.png

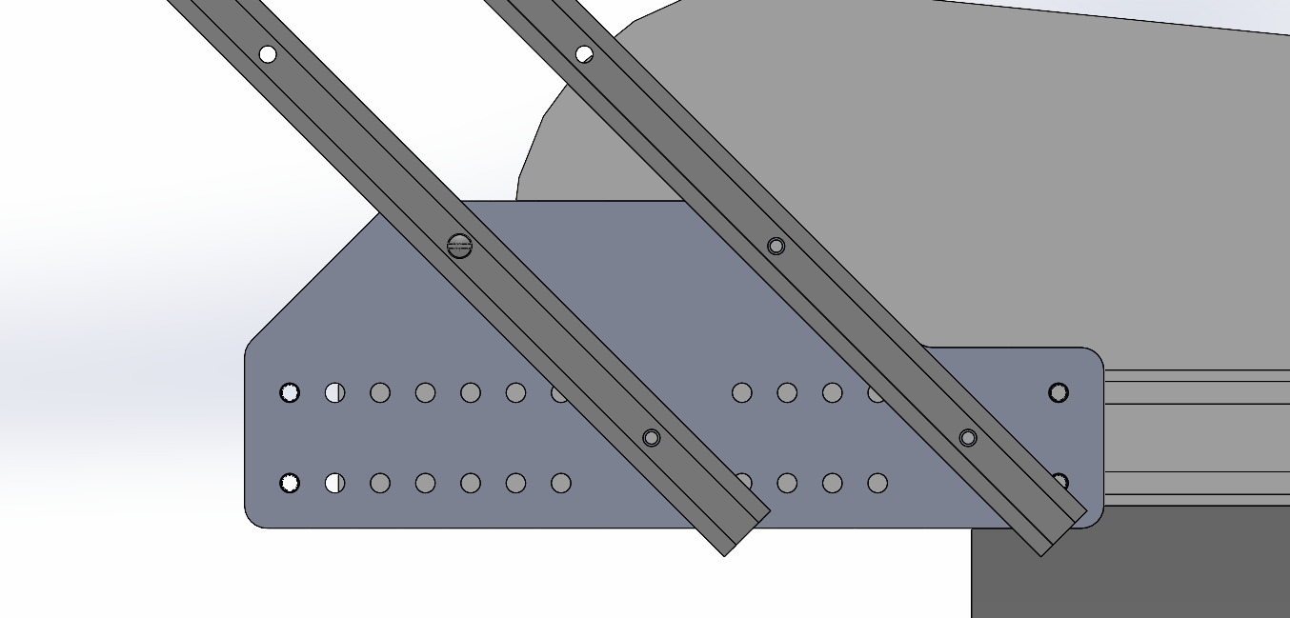
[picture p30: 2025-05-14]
CADFiles&Drawings/DXF and PDF Files/Reference Images/SlidingPlateView1.png

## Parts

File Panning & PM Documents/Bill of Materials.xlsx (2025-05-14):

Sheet: Sheet1
 |  |  |  |  |  |  | Level-1: Electronics
Team Number |  | 205 |  |  |  |  | Level-2: Waterproofing
Team Name |  | Robotic Arm to Assist Motorized Chair Users |  |  |  |  | Level-3: Mounting
Total Cost |  | $1147.62 |  |  | Bill of Materials |  | Level-4: 3D Printed
 |  |  |  |  | Taxes and Shipping NOT included |  | Level-5: Hardware
 |  |  |  |  |  |  | Level-6: Other
BOM Level | Part Name |  | Part Number | Part Details |  | Unit Cost | Quantity (Ea./Pkg.) |  | Total Cost | Procurement Details | Additional Notes
Level-1 | Waveshare Roarm |  | RoArm-M2-S |  |  | $223.99 | 1 | Ea. | $223.99 | Amazon (https://www.amazon.com/Waveshare-High-Torque-Expansion-Secondary-Development/dp/B0CMLNPH8V?asc_campaign=ff27c2af69359fb71bbfcc193b2835d4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) | Direct Order
Level-1 | Joystick |  | HE2 SERIES 3 AXIS | Base(metal housing), Handle(two buttons), Limiter(square), Outout(0-5V), and Color(grey) |  | $290.07 | 1 | Ea. | $290.07 | Ruffy Controls (https://ruffycontrols.com/product/he2-series-3-axis/) | Direct Order
Level-1 | Buttons |  | B0C2G4RC4Q | Size(momentary) and Color(silver) |  | $12.49 | 5 | Pkg. | $62.45 | Amazon (https://www.amazon.com/gp/product/B0C2G4RC4Q/ref=ewc_pr_img_4?smid=A1JR6G2R07EO7U&th=1) | Direct Order
Level-1 | Switches |  | B0CKXRHJPF | Type(5pcs switch + switch holder) |  | $8.09 | 2 | Pkg. | $16.18 | Amazon (https://www.amazon.com/gp/product/B0CKXRHJPF/ref=ewc_pr_img_2?smid=ATVPDKIKX0DER&th=1) | Direct Order
Level-1 | Wires |  | 1311 | 22AWG Solid Core |  | $15.95 | 1 | Ea. | $15.95 | Adafruit (https://www.adafruit.com/product/1311) | Direct Order
Level-1 | Heat Shrink Tubing |  | asd-123 | Heat Shrink Tube Kit with Box(5 colors/12 Sizes) |  | $6.99 | 1 | Pkg. | $6.99 | Amazon (https://www.amazon.com/560PCS-Heat-Shrink-Tubing-Eventronic/dp/B072PCQ2LW) | Direct Order
Level-1 | Male-Male Plug Cable |  | B0BN2YX895 | Voltage(12V) and Input Current(1.5A) |  | $8.99 | 1 | Pkg. | $8.99 | Amazon (https://www.amazon.com/GINTOOYUN-Adapter-Extension-Surveillance-Security/dp/B0BN2YX895) | Direct Order
Level-1 | Battery |  | PB120B1 | 12V Lithium ion |  | $81.99 | 1 | Pkg. | $81.99 | Amazon (https://www.amazon.com/TalentCell-PB120B1-Rechargeable-38400mAh-142-08Wh/dp/B07H8F5HYJ?mcid=4d9721f459d23e829a73bdaec0a33bbe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) | Direct Order
Level-2 | Sleeve Cover |  | B0D6Y2R9LZ | Color(black+blue) and Material(PU leather) |  | $9.56 | 1 | Pkg. | $9.56 | Amazon (https://www.amazon.com/Waterproof-Protector-Oilproof-Oversleeves-Protection/dp/B089K2JLGK?mcid=db1de4c9f36636f38d4ba4db89535c1c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) | Direct Order
Level-2 | Hole Plugs |  | suiwotin - 220105 - 7 | Color(white) and Size(1/4") |  | $6.99 | 1 | Pkg. | $6.99 | Amazon (https://www.amazon.com/dp/B09Q2RK9LG?s=kitchen&sp_csd=d2lkZ2V0TmFtZT1zcF9kZXRhaWxfdGhlbWF0aWM) | Direct Order
Level-2 | Silicon Gasket Maker |  | B0CXPXLCCH | Size(3 Fl. Oz.) and Style (Ultra Black) |  | $14.96 | 1 | Pkgs. | $14.96 | Amazon (https://www.amazon.com/Permatex-82180-Maximum-Resistance-Silicone/dp/B0CXPXLCCH?s=automotive) | Direct Order
Level-3 | Sliding Plate |  |  | Material(Al.) and Thickness(1/4") |  | $52.42 | 1 | Ea. | $52.42 |  | Additional Manufacturing
Level-3 | Connecting Plate |  |  | Material(Al.) and Thickness(1/8") |  | $26.47 | 1 | Ea. | $26.47 |  | Additional Manufacturing
Level-3 | Fixturing T-Track |  | 1850A11 | Length(18") |  | $9.83 | 2 | Ea. | $19.66 | McMaster (https://www.mcmaster.com/1850A11/) | Direct Order
Level-3 | French Cleats |  | 2152A11 | Material(Al.) |  | $8.24 | 1 | Pkg. | $8.24 | McMaster (https://www.mcmaster.com/2152A11/) | Direct Order
Level-4 | 3D-Prints |  |  | Material(ABS) |  | $101.26 | 1 | Pkg. | $101.26 |  | Additional Manufacturing
Level-5 | Heat-Set Inserts for Plastic |  | 94459A340 | Brass, 10-32 Thread Size, 1/4" Installed Length |  | $12.36 | 1 | Pkg. | $12.36 | McMaster (https://www.mcmaster.com/94459A340/) | Direct Order
Level-5 | 316 Stainless Steel Button Head Hex Drive Screw |  | 98164A178 | Super-Corrosion-Resistant, 10-32 Thread Size, 1/2" Long |  | $9.82 | 1 | Pkg. | $9.82 | McMaster (https://www.mcmaster.com/98164A178/) | Direct Order
Level-5 | Male-Female Threaded Hex Standoff |  | 91075A467 | 18-8 Stainless Steel, 3/16" Hex, 5/16" Long, 6-32 to 6-32 Thread |  | $3.79 | 1 | Ea. | $3.79 | McMaster (https://www.mcmaster.com/91075A467/) | Direct Order
Level-5 | 18-8 Stainless Steel Pan Head Slotted Screws |  | 91792A144 | 6-32 Thread Size, 1/4" Long |  | $5.51 | 1 | Pkg. | $5.51 | McMaster (https://www.mcmaster.com/91792A144/) | Direct Order
Level-5 | Lock Nut for T-Track |  | 1850A26 | Steel, 3/4" |  | $3.38 | 2 | Ea. | $6.76 | McMaster (https://www.mcmaster.com/1850A26/) | Direct Order
Level-5 | Low-Strength Steel Square Nut |  | 96887A319 | Class 5, Zinc-Plated, M6 x 1 mm Thread |  | $14.40 | 1 | Pkg. | $14.40 | McMaster (https://www.mcmaster.com/96887A319/) | Direct Order
Level-5 | Alloy Steel Socket Head Screw |  | 91290A017 | Black-Oxide, M2 x 0.4 mm Thread, 10 mm Long |  | $15.56 | 1 | Pkg. | $15.56 | McMaster (https://www.mcmaster.com/91290A017/) | Direct Order
Level-5 | High-Strength Steel Nylon-Insert Locknut |  | 94645A102 | Class 10, Zinc Plated, M5 x 0.8 mm Thread, 5 mm High |  | $16.62 | 1 | Pkg. | $16.62 | McMaster (https://www.mcmaster.com/94645A102/) | Direct Order
Level-5 | Low-Strength Steel Nylon-Insert Locknut |  | 90633A007 | Thin-Profile, Zinc-Plated, 6-32 Thread Size |  | $10.20 | 1 | Pkg. | $10.20 | McMaster (https://www.mcmaster.com/90633A007/) | Direct Order
Level-5 | Stainless Steel Wing-Head Thumb Screw |  | 92625A413 | M6 x 1mm Thread Size, 12mm Long |  | $4.44 | 4 | Ea. | $17.76 | McMaster (https://www.mcmaster.com/92625A413/) | Direct Order
Level-6 | Acrylic Panel |  |  | Color(White Opaque) and Thickness(1/8") |  | $76.68 | 1 | Pkg. | $76.68 |  | Additional Manufacturing
Level-6 | Portable Cupholder |  | B0CKGM1G9M | Color(Black Reflective) |  | $11.99 | 1 | Ea. | $11.99 | Amazon (https://www.amazon.com/Katsia-ParaSipper-Beverage-Cup-Holder/dp/B0CJ7YMR34) | Direct Order
 |  |  |  |  |  |  | Total |  | $1147.62

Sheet: Sheet2
Additional Manufacturing
BOM Level | Part Name | Manufacturing Process | Manufacturing Cost/Quote | Recomendations
Level-3 | Sliding Plate | CNC and Plasma Cutting | $52.42
Level-3 | Connecting Plate | CNC and Plasma Cutting | $26.47
Level-4 | End Effector Cover | 3D-Printing | $6.99 | Infil (60%)
Level-4 | Waterproofing | 3D-Printing | $5.99 | Infill (60%)
Level-4 | Corner Frame | 3D-Printing | $63.80 | Infill (100%)
Level-4 | Pin | 3D-Printing | $5.99 | Infill (100%)
Level-4 | Power Bank Case | 3D-Printing | $28.66 | Infill (50%)
Level-4 | Stopping Plate | 3D-Printing | $6.99 | Infill (100%)
Level-4 | Battery Cover | 3D-Printing | $5.99 | Infill (100%)
Level-4 | Cylindrical Guide_Male | 3D-Printing | $6.49 | Infill (60%)
Level-4 | Cylindrical Guide_Female | 3D-Printing | $6.99 | Infill (60%)
Level-4 | Armrest Attachment | 3D-Printing | $11.04 | Infill (100%)
Level-6 | Acrylic Panel | Laser Cutting | $76.68
Please Note the Following:
1. These prices may vary depending on manufacturer specifications such as deburring, tapping, color, infill, etc.
2. The listed quotes use the recommened notes as the manufacuterer specifications
3. The 3D-Prints quote from Sheet1 differs from the sum total of the 3D-printing quotes on Sheet2
3. For additional guidance, please refer to "Part Manufacturing Manual"

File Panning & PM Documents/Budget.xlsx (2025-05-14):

Budget - 205 - Robotic Arm to Assist Motorized Wheelchair Users
Starting Budget = | $5000.00 |  |  |  | Est. Shipping Cost= | -$140.36 |  |  |  |  |  |  |  |  |  | Definitions / Variables
Projected Budget = | $3419.82 |  |  |  | Projected Used Budget = | -$1580.18 | Verification
Available Budget = | $3419.82 |  |  |  | Used Budget = | -$1580.18 | -$1267.18
Item description | Part # | URL | Vendor | Quantity | Price Per Unit (No ship or tax) | Total Cost | Status (OPEN/PURCHASED) | Received (Y/N) | Month Purchased | Nov | Dec | Jan | Feb | Mar | April | Projected Used Budget | Shows the budget used regardless of whether item has been purchased yet or not
Permobil UniTrack Bar 17-19" seat depth | SKU: 321440 | https://buildmywheelchair.com/unitrack-bar-17-18-19-seat-depth-corpus-3g-vs/ | Build My Wheelchair | 1 | $48.00 | $48.00 | PURCHASED | Y | November | $380.97 | $0.00 | $127.48 | $934.49 | $240.18 | $200.00 | Used Budget | Shows the budget actually used through completed purchases
Waveshare High-torque Serial Bus Servo, RoArm-M2-S Desktop Robotic Arm Kit, Based On ESP32, 4-DOF | SKU:25118 Part No.:RoArm-M2-S | https://www.waveshare.com/product/robotics/robot-arm-control/robot-arm/roarm-m2-s.htm?sku=25118 | Waveshare | 1 | $223.99 | $223.99 | PURCHASED | Y | November |  |  |  | $200.00 | $200.00 | $200.00 | Verification | Verifies the used budget with a different formula
1/4" Thick 6061 Aluminum Sheet & Plate 1x1ft | P314T6 | https://www.metalsdepot.com/aluminum-products/6061-aluminum-sheet-plate | Metals Depot | 1 | $46.60 | $46.60 | PURCHASED | Y | January | $380.97 | $380.97 | $508.45 | $1442.94 | $1683.12 | $1883.12 | Received | Once we receive item, change received to "Y"
4-Axis Joystick | JH-D400X-R4 | https://www.amazon.com/SaiDian-4-Axis-Joystick-Potentiometer-JH-D400X-R4/dp/B08CGYGMJL | Amazon | 1 | $17.89 | $17.89 | PURCHASED | Y | November | $5000.00 | $5000.00 | $5000.00 | $5000.00 | $5000.00 | $5000.00 | Available Budget | Shows the remaining budget after purchases are made
Talentcell 12V Lithium ion Battery | PB120B1 | https://www.amazon.com/TalentCell-PB120B1-Rechargeable-38400mAh-142-08Wh/dp/B07H8F5HYJ?mcid=4d9721f459d23e829a73bdaec0a33bbe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 | Talentcell | 1 | 91.09 | $91.09 | PURCHASED | Y | November |  |  |  |  |  |  | Instructions
18" Long T-Track Fixturing Track | 1850A11 | https://www.mcmaster.com/1850A11/ | McMaster | 2 | $9.83 | $19.66 | PURCHASED | Y | January |  |  |  |  |  |  | 1 | Enter item description, part #, and link to vendor
1" Long Hex Head Screw for Fixturing Track (10 count) | 1850A22 | https://www.mcmaster.com/1850A22/ | McMaster | 1 | $1.66 | $1.66 | PURCHASED | Y | January |  |  |  |  |  |  | 2 | Enter qunatity and price per unit
Steel, 3/4" Diameter Lock Nut for Fixturing Track | 1850A26 | https://www.mcmaster.com/1850A26/ | McMaster | 2 | $3.25 | $6.50 | PURCHASED | Y | January |  |  |  |  |  |  | 3 | Add to cart and go through purchase process without purchasing to determine tax and shipping
18-8 Stainless Steel Pan Head Slotted Screws (100 count) | 91792A144 | https://www.mcmaster.com/91792A144/ | McMaster | 1 | $5.74 | $5.74 | PURCHASED | Y | January |  |  |  |  |  |  | 4 | Enter shipping method if applicable (for Cory)
1/8" Thick 6061 Aluminum Sheet & Plate 1x1ft | S318T6 | https://www.metalsdepot.com/aluminum-products/6061-aluminum-sheet-plate | Metals Depot | 1 | $47.32 | $47.32 | PURCHASED | Y | January |  |  |  |  |  |  | 5 | Total cost is calculated in spreadsheet, validate the value against what the website says
Car Shift Boot Cover | ‎607311_1_0hBkZUDM | https://www.amazon.com/InnoHHustle-Universal-Replacement-Waterproof-Handbrake/dp/B0DG8ZPX1Q?s=automotive&xpid=WxD8ym98_NuLP | InnoHHustle | 1 | $5.95 | $5.95 | PURCHASED | Y | February |  |  |  |  |  |  | 6 | Send order to Cory
WaterProof Sleeve | B089K2JLGK | https://www.amazon.com/Waterproof-Protector-Oilproof-Oversleeves-Protection/dp/B089K2JLGK?mcid=db1de4c9f36636f38d4ba4db89535c1c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 | Amazon | 1 | $9.99 | $9.99 | PURCHASED | Y | February |  |  |  |  |  |  | 7 | Once Cory confirms order, change status to "PURCHASED"
Waveshare 30KG Serial Bus Servo | ST3215 Servo | https://www.amazon.com/Precision-Programmable-Magnetic-Feedback-Switchable/dp/B0BZLFJL9S | Waveshare | 2 | $30.90 | $61.80 | PURCHASED | Y | February |  |  |  |  |  |  | 9 | Send Meriam the reciept sent with the item
Heat-Set Inserts for Plastic | 94459A340 | https://www.mcmaster.com/94459A340/ | McMaster | 3 | $12.36 | $37.08 | PURCHASED | Y | February
Nutsert Screws | 98164A178 | https://www.mcmaster.com/98164A178/ | McMaster | 2 | $9.82 | $19.64 | PURCHASED | Y | February
Easy-Level Lift-Off Panel-Hanging Bracket | 2152A11 | https://www.mcmaster.com/2152A11/ | McMaster | 1 | $8.24 | $8.24 | PURCHASED | Y | February
Male-Female Threaded Hex Standoff | 91075A467 | https://www.mcmaster.com/91075A467/ | McMaster | 1 | $3.62 | $3.62 | PURCHASED | Y | February
5pc Momentary Push Button Switch; Color: (Silver) Size: (Momentary) | B0C2G4RC4Q | https://www.amazon.com/gp/product/B0C2G4RC4Q/ref=ewc_pr_img_4?smid=A1JR6G2R07EO7U&th=1 | Amazon | 2 | $12.49 | $24.98 | PURCHASED | Y | February
Nilight 5pcs round rocket switches | B0CKXRHJPF | https://www.amazon.com/gp/product/B0CKXRHJPF/ref=ewc_pr_img_2?smid=ATVPDKIKX0DER&th=1 | Amazon | 1 | $8.09 | $8.09 | PURCHASED | Y | February
Silicon Gasket Maker (3 fl. oz, pack of 2, style: ultra black) | B0CXPXLCCH | https://www.amazon.com/Permatex-82180-Maximum-Resistance-Silicone/dp/B0CXPXLCCH?s=automotive | Amazon | 1 | $14.96 | $14.96 | PURCHASED | Y | February
Seal Self Fusing Silicone Tape | B08B3JSJF3 | https://www.amazon.com/Seal-Self-Fusing-Silicone-Tape/dp/B08B3JSJF3?sp_csd=d2lkZ2V0TmFtZT1zcF9hdGY | Amazon | 1 | $9.99 | $9.99 | PURCHASED | Y | February
90 Degree Male to Male Plug Cable | B0BN2YX895 | https://www.amazon.com/GINTOOYUN-Adapter-Extension-Surveillance-Security/dp/B0BN2YX895 | Amazon | 1 | $8.99 | $8.99 | PURCHASED | Y | February
Button Head Hex Drive Screw | 92095A211 | https://www.mcmaster.com/92095A211/ | McMaster | 1 | $10.01 | $10.01 | PURCHASED | Y | February
Fully Threaded T-Slot Nut | 90510A232 | https://www.mcmaster.com/90510A232/ | McMaster | 6 | $1.94 | $11.64 | PURCHASED | Y | February
18-8 Stainless Steel Washer | 92141A029 | https://www.mcmaster.com/92141A029/ | McMaster | 1 | $5.50 | $5.50 | PURCHASED | Y | February
L-Channel (2ft) | 8982K124 | https://www.mcmaster.com/products/l-channels/multipurpose-6061-aluminum-90-angles-7/ | McMaster | 1 | $24.92 | $24.92 | PURCHASED | Y | February
Alloy Steel Socket Head Screw | 91290A017 | https://www.mcmaster.com/91290A017/ | McMaster | 1 | $15.56 | $15.56 | PURCHASED | Y | February
High-Strength Steel Nylon-Insert Locknut | 94645A102 | https://www.mcmaster.com/94645A102/ | McMaster | 1 | $16.62 | $16.62 | PURCHASED | Y | February
Stainless Steel Wing-Head Thumb Screw (M6) | 92625A413 | https://www.mcmaster.com/92625A413/ | McMaster | 4 | $4.44 | $17.76 | PURCHASED | Y | February
Low-Strength Steel Thin Nylon-Insert Locknut | 90633A007 | https://www.mcmaster.com/90633A007/ | McMaster | 1 | $10.20 | $10.20 | PURCHASED | Y | February
Low-Strength Steel Square Nut | 96887A319 | https://www.mcmaster.com/96887A319/ | McMaster | 1 | $14.40 | $14.40 | PURCHASED | Y | February
Electrocookie PCB | B07ZYTZ48N | https://www.amazon.com/ElectroCookie-Snappable-Arduino-Electronics-Gold-Plated/dp/B07ZYTZ48N | Amazon | 1 | $9.99 | $9.99 | PURCHASED | Y | February
JST PH 2-Pin Cable - Female Connector | 261 | https://www.adafruit.com/product/261 | Adafruit | 3 | $0.75 | $2.25 | PURCHASED | Y | February
Drill & Tap Set | 1765531 | https://www.lowes.com/pd/IRWIN-HANSON-SAE-2-Pack-Tap-and-Drill-Set/1003087522?store=447&ds_a_cid=279391351&gad_source=1&gclsrc=aw.ds | IRWIN | 1 | $5.98 | $5.98 | PURCHASED | Y | February
Acrylic Panel | N/A | https://www.canalplastic.com/products/7508-white-opaque-acrylic-sheet?variant=32920759246 | Canal Plastic | 4 | $7.35 | $29.40 | PURCHASED | Y | February
Fixed Cupholder | ‎OH-001 | https://www.amazon.com/Nearly-Universal-OH-Wheelchair-Holder/dp/B001YJGDY8?gQT=1 | Amazon | 1 | $21.95 | $21.95 | PURCHASED | Y | February
Canvas Cupholder | CDC1327 | a (https://www.mobility-aids.com/product.asp?itemid=6682&gad_source=1) | Mobilty Aids | 1 | $29.95 | $29.95 | PURCHASED | Y | February
Adafruit ESP32 Feather V2 | 5900 | https://www.adafruit.com/product/5900 | Adafruit | 2 | $20.95 | $41.90 | PURCHASED | Y | February
Hook-up Wire Spool Set | 1311 | https://www.adafruit.com/product/1311 | Adafruit | 1 | $15.95 | $15.95 | PURCHASED | Y | February
Male-Female Headers | 5583 | https://www.adafruit.com/product/5583 | Adafruit | 2 | $0.95 | $1.90 | PURCHASED | Y | February
Male-Male Headera | 5584 | https://www.adafruit.com/product/5584 | Adafruit | 2 | $0.95 | $1.90 | PURCHASED | Y | February
2x23 Male Headers | 2076 | https://www.adafruit.com/product/2076 | Adafruit | 2 | $1.50 | $3.00 | PURCHASED | Y | February
560PCS Heat Shrink Tubing | asd-123 | https://www.amazon.com/560PCS-Heat-Shrink-Tubing-Eventronic/dp/B072PCQ2LW | Amazon | 1 | $6.39 | $6.39 | PURCHASED | Y | February
Waveshare High-torque Serial Bus Servo, RoArm-M2-S Desktop Robotic Arm Kit, Based On ESP32, 4-DOF | SKU:25118 Part No.:RoArm-M2-S | https://www.waveshare.com/product/robotics/robot-arm-control/robot-arm/roarm-m2-s.htm?sku=25118 | Waveshare | 1 | $223.99 | $223.99 | PURCHASED | Y | February
Leather Cupholder | N/A | https://www.jasonsherron.com/product-page/ready-made-leather-calf-takeaway-cup-holder | Jason & Sherron | 1 | $28.19 | $28.19 | PURCHASED | Y | March
Paracord Cupholder | B0CKGM1G9M | https://www.amazon.com/Katsia-ParaSipper-Beverage-Cup-Holder/dp/B0CJ7YMR34 | Amazon | 1 | $11.99 | $11.99 | PURCHASED | Y | March
Expensive Joystick | HE2 | https://ruffycontrols.com/product/he2-series-3-axis/ | Ruffy Controls | 1 | $290.07 | $290.07 | PURCHASED | Y | March
(1/4") White Hole Plugs | suiwotin - 220105 - 7 | https://www.amazon.com/dp/B09Q2RK9LG?s=kitchen&sp_csd=d2lkZ2V0TmFtZT1zcF9kZXRhaWxfdGhlbWF0aWM | Amazon | 1 | $6.99 | $6.99 | PURCHASED | Y | March
Aluminum Stick Electrode | E4043 | https://www.forneyind.com/forney-45889-e4043-aluminum-electrode-1-8-in-x-1-2-pound | Forney | 1 | $31.99 | $31.99 | OPEN | N | Eliminated
Gorilla All Weather Outdoor Waterproof Duct Tape | 6009002 | https://www.amazon.com/Gorilla-Weather-Waterproof-Temperature-Resistant/dp/B09WB29W9Z | Gorrila | 1 | $25.96 | $25.96 | OPEN | N | Eliminated
Corner Reinforcing Brackets | 1088A31 | https://www.mcmaster.com/1088A31/ | McMaster | 10 | $3.92 | $39.20 | OPEN | N | Eliminated
Rubber Gasket fit 3/32" 20' length |  | https://www.amazon.com/Rubber-Channel-Protector-Length-Shaped/dp/B0BN3HZKY1?mcid=9bcbbe47a7b634ab949f484885b9e626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 | Protalwell | 1 | $15.99 | $15.99 | OPEN | N | Eliminated
Cornersunk Black-Oxide Alloy Steel Screws 4-48, 3/8" (25 count) | 91253A142 | https://www.mcmaster.com/91253A142/ | McMaster | 3 | $10.76 | $32.28 | OPEN | N | Eliminated
18-8 Stainless Steel Nylon-Insert Locknut (25 count) | 91831A173 | https://www.mcmaster.com/91831A173/ | McMaster | 3 | $4.72 | $14.16 | OPEN | N | Eliminated
Universal Shifter Boot | B07G5GTY17 | https://www.amazon.com/Universal-Manual-Cover%EF%BC%8CPU-Leather-Shifter/dp/B07G5GTY17?mcid=e6084ad6d036324dba99cb91fea15ffc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 | Amazon | 1 | $9.06 | $9.06 | OPEN | N | Eliminated
Drake Muscle Cars Shifter Boot | 425716 | https://www.americanmuscle.com/scott-drake-mustang-shifter-boot-leather-e7zz-7277-a.html?T5_Var4=425716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 | AmericanMuscle | 1 | $32.87 | $32.87 | OPEN | N | Eliminated
WaterProof Sleeve | B0D6Y2R9LZ | https://www.amazon.com/dp/B0CR1KFP37?s=apparel&sp_csd=d2lkZ2V0TmFtZT1zcF9kZXRhaWwy | Amazon | 1 | $9.99 | $9.99 | OPEN | N | Eliminated
2 in Dia 3:1 Waterproof Heat Shrink Tubing Kit | ASIN ‏ : ‎ B07VSYB41Y | https://www.amazon.com/inch-Waterproof-Shrinkable-Insulation-Wear-Resistant/dp/B07VSYB41Y?cv_ct_cx=waterproof%2Bheat%2Bshrink%2Btubing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 | Amazon: YUSKY | 1 | $13.89 | $13.89 | OPEN | N | Eliminated
Lipo Battery Charger Hitec |  | https://maxamps.com/collections/lipo-battery-charger/products/lipo-battery-charger-hitec-rdx1-200-ac-dc-charger-discharger | Maxamps | 1 | $79.00 | $79.00 | OPEN | N | Eliminated
Arduino Uno R3 USB Microcontroller | SKU: RB-Ard-34 | https://www.robotshop.com/products/arduino-uno-r3-usb-microcontroller | RobotShop | 1 | $27.60 | $27.60 | OPEN | N | Eliminated
Arduino Uno Rev4 Wifi | SKU: RB-Ard-187 | https://www.robotshop.com/products/arduino-uno-rev4-wifi | RobotShop | 1 | $30.07 | $30.07 | OPEN | N | Eliminated
Arduino Mega 2560 Microcontroller REv3 | SKU: RB-Ard-33 | https://www.robotshop.com/products/arduino-mega-2560-microcontroller-rev3 | RobotShop | 1 | $48.40 | $48.40 | OPEN | N | Eliminated
Permobil UniTrack Bar 14-16" seat depth | SKU: 321434 | https://buildmywheelchair.com/unitrack-bar-14-15-16-seat-depth-corpus-3g-vs/ | Build My Wheelchair | 1 | $48.00 | $48.00 | OPEN | N | Eliminated
Graphene LiPo 5200 3S 11.1v Battery Pack | SKU: Graphene- Lipo-5200-3S-Pack-2 | https://maxamps.com/collections/3s-lipo-battery-11-1v/products/graphene-lipo-5200-3s-11-1v-battery | Maxamps | 1 | $134.00 | $134.00 | OPEN | N | Eliminated
3S Lipo Battery 11.1V 80C 5200mAh (2 pack) | B0BZKYGL1N | https://www.amazon.com/EMEPOVGY-Battery-5200mAh-Connector-Vehicles/dp/B0BZKYGL1N?asc_campaign=ff27c2af69359fb71bbfcc193b2835d4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 | Amazon | 1 | $39.99 | $39.99 | OPEN | N | Eliminated

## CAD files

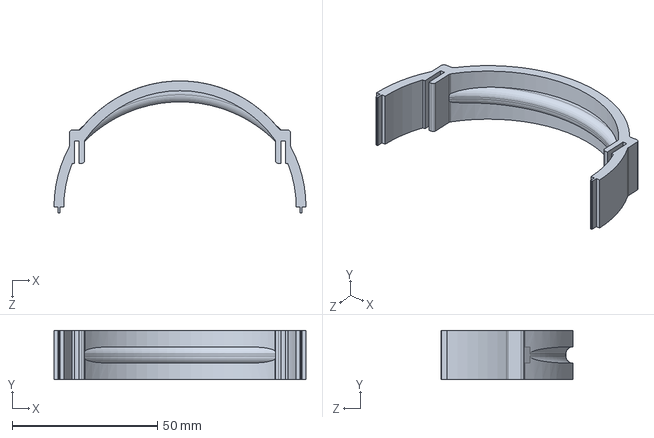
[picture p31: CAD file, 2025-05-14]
CADFiles&Drawings/CAD Files/Case/ABS 3D Print/Cylindrical Guide_Male.SLDPRT
86.7 x 17.0 x 45.5 mm

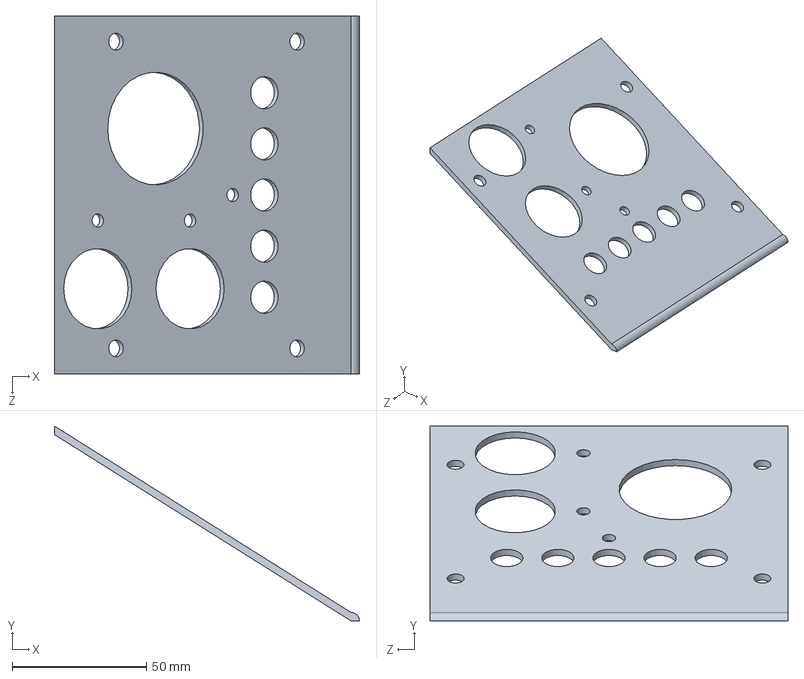
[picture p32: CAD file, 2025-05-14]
CADFiles&Drawings/CAD Files/Case/Acrylic Case Plates/Diagonal Plate.SLDPRT
113.7 x 72.6 x 133.4 mm

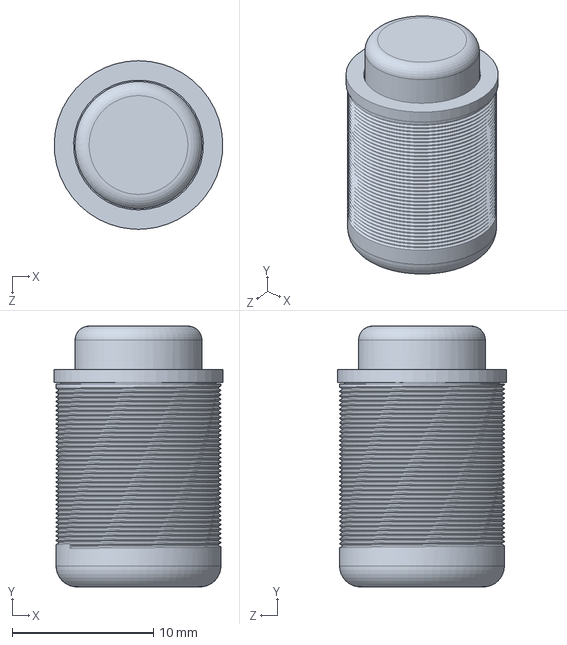
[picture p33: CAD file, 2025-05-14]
CADFiles&Drawings/CAD Files/Case/Electronics/Button/Button.SLDPRT
11.9 x 18.5 x 12.0 mm

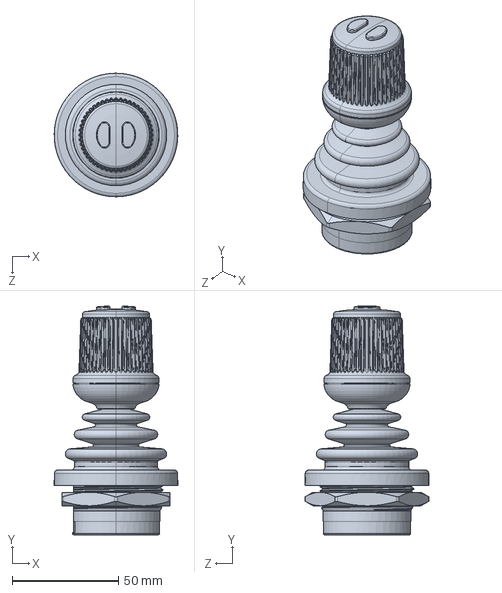
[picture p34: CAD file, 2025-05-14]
CADFiles&Drawings/CAD Files/Case/Electronics/Joystick.SLDPRT
58.0 x 107.5 x 58.2 mm

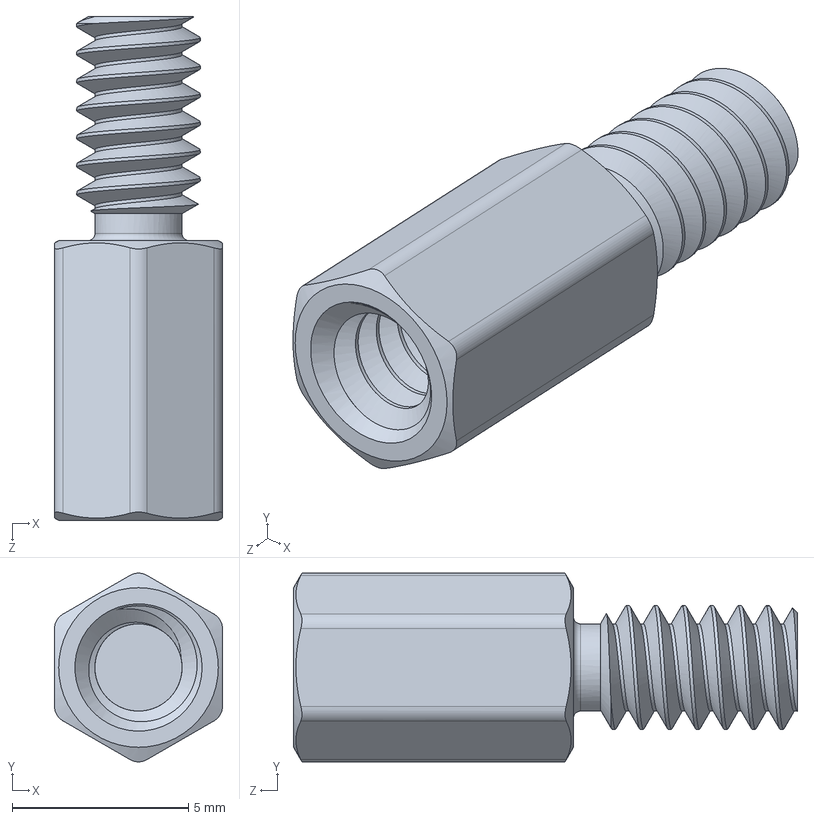
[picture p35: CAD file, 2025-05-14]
CADFiles&Drawings/CAD Files/Case/Hardware/Standoff.SLDPRT
4.76 x 5.35 x 14.3 mm

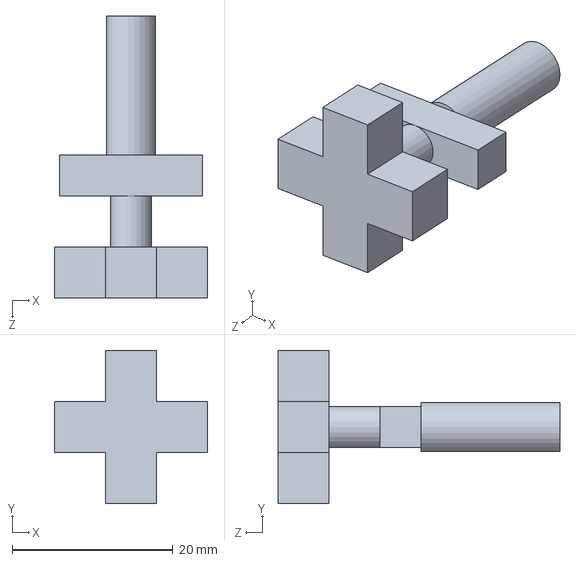
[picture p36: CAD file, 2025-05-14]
CADFiles&Drawings/CAD Files/Mounting/Connecting Assembly/ABS 3D Print/Pin.SLDPRT
19.1 x 19.1 x 35.1 mm

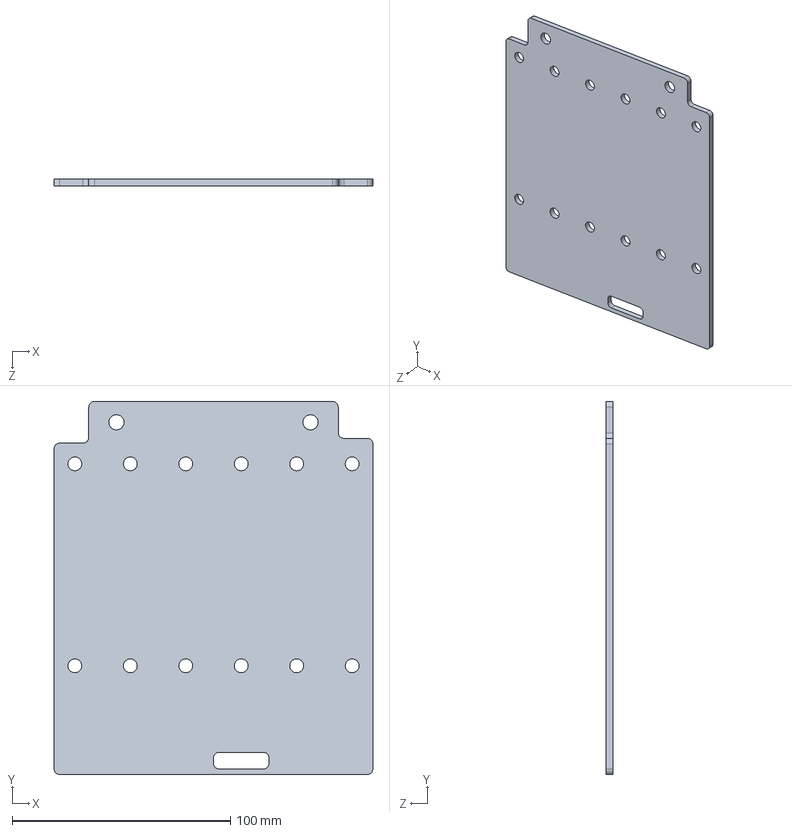
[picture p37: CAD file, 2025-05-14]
CADFiles&Drawings/CAD Files/Mounting/Connecting Assembly/Eigth Inch Aluminum/Connecting Plate.SLDPRT
146.1 x 170.9 x 3.17 mm

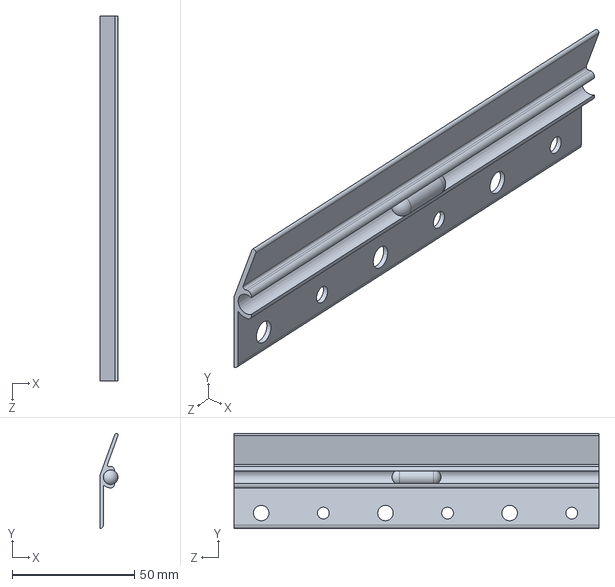
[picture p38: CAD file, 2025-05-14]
CADFiles&Drawings/CAD Files/Mounting/Connecting Assembly/Hardware/French Cleat lower.SLDPRT
7.42 x 38.9 x 149.3 mm

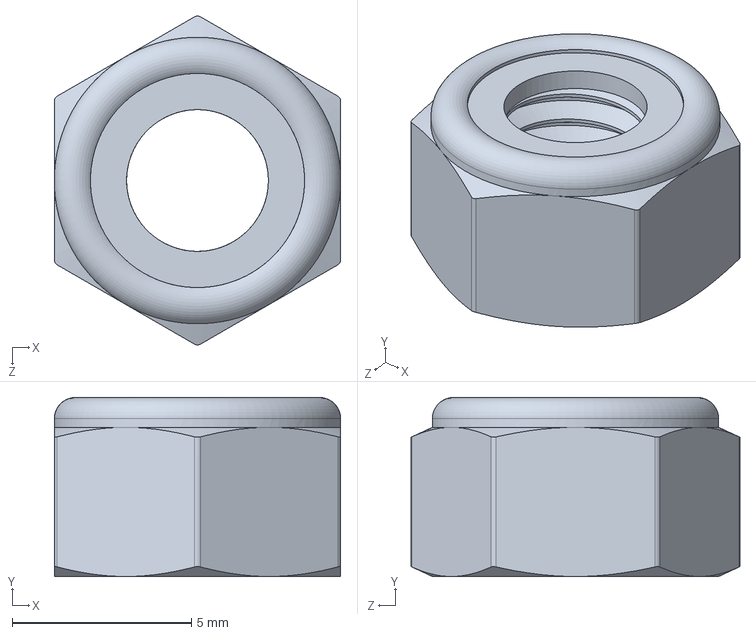
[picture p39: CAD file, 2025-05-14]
CADFiles&Drawings/CAD Files/Mounting/Connecting Assembly/Hardware/Nuts/Button Head Locknuts.SLDPRT
8.00 x 5.00 x 9.19 mm

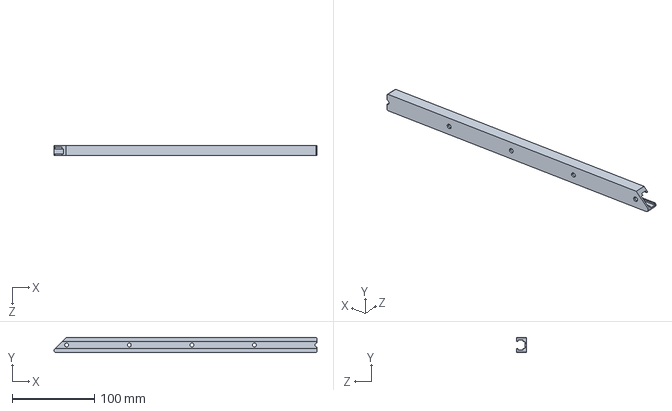
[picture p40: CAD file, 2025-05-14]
CADFiles&Drawings/CAD Files/Mounting/Unitrack Mounting Assembly/Hardware/Shortened Rail.SLDPRT
320.3 x 18.3 x 12.2 mm

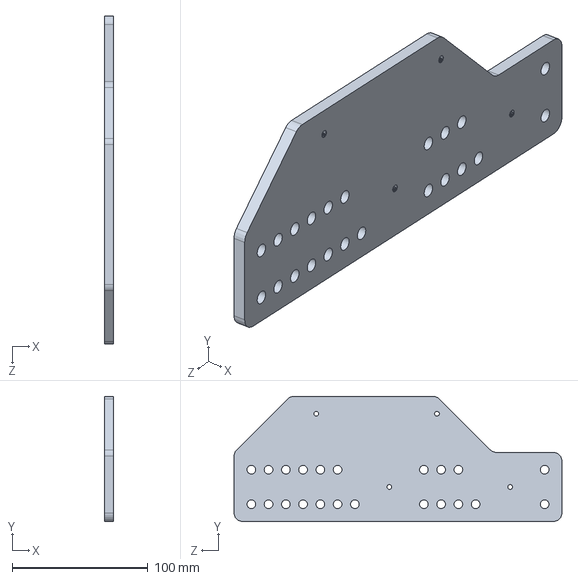
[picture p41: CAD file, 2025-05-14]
CADFiles&Drawings/CAD Files/Mounting/Unitrack Mounting Assembly/Quarter Inch Aluminum/Sliding Plate.SLDPRT
6.35 x 92.0 x 241.3 mm

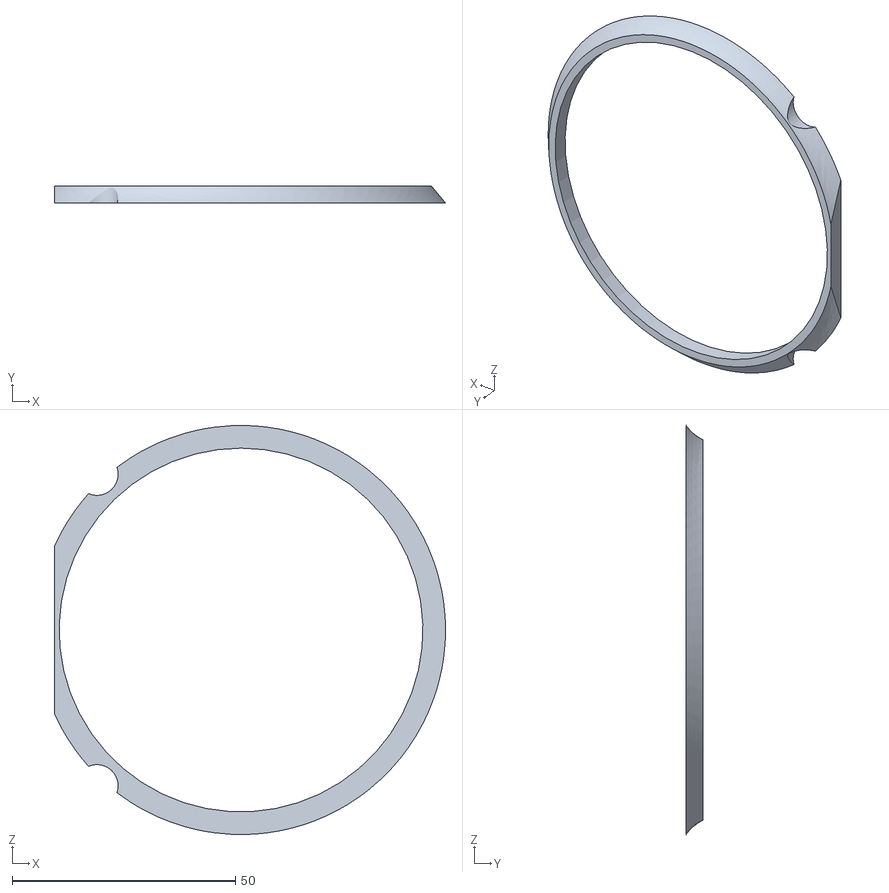
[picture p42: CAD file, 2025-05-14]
CADFiles&Drawings/CAD Files/Outsourcing Parts/3D Printing (STL Files)/WaterProofing.STL
87.7 x 3.81 x 91.7

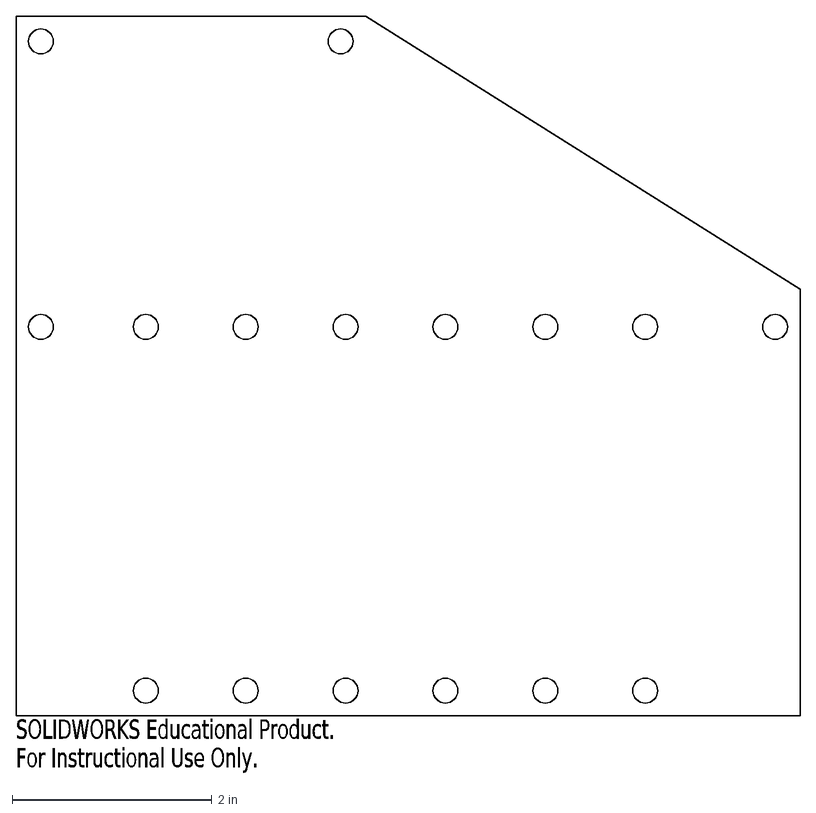
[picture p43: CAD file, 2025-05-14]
CADFiles&Drawings/CAD Files/Outsourcing Parts/Acrylic Lasercutting (DXF Files)/DXF Drawing/Side Plate.DXF
SOLIDWORKS Educational Product.
For Instructional Use Only.

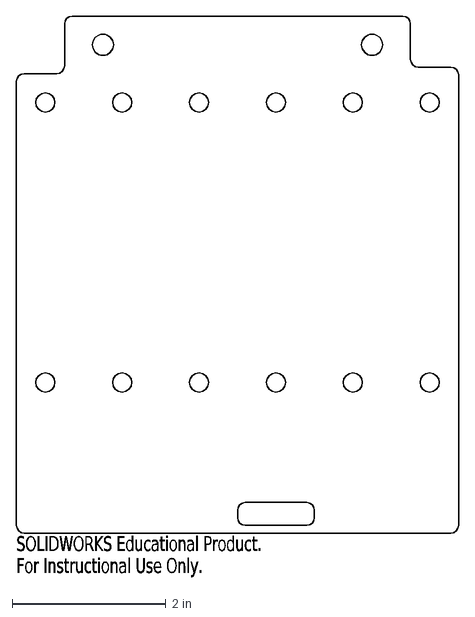
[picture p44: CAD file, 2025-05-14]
CADFiles&Drawings/CAD Files/Outsourcing Parts/Aluminium Lasercutting (DXF Files)/DXF Drawing/Connecting Plate.DXF
SOLIDWORKS Educational Product.
For Instructional Use Only.

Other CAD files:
CADFiles&Drawings/CAD Files/Case/Electronics/Switch/Switch.SLDASM
CADFiles&Drawings/CAD Files/Mounting/Connecting Assembly/Connecting Assembly.SLDASM
CADFiles&Drawings/CAD Files/Mounting/Unitrack Mounting Assembly/Mounting Assembly.SLDASM
CADFiles&Drawings/CAD Files/Wheelchair/Permobil_M3_Assembly.SLDASM
CADFiles&Drawings/CAD Files/Case/ABS 3D Print/Armrest.SLDPRT
CADFiles&Drawings/CAD Files/Case/ABS 3D Print/Battery Cover.SLDPRT
CADFiles&Drawings/CAD Files/Case/ABS 3D Print/Corner Frame.SLDPRT
CADFiles&Drawings/CAD Files/Case/ABS 3D Print/Cylindrical Guide_Female.SLDPRT
CADFiles&Drawings/CAD Files/Case/ABS 3D Print/EndEffector_Cover.SLDPRT
CADFiles&Drawings/CAD Files/Case/ABS 3D Print/PowerBank_Case.SLDPRT
CADFiles&Drawings/CAD Files/Case/ABS 3D Print/Stopping Plate.SLDPRT
CADFiles&Drawings/CAD Files/Case/ABS 3D Print/WaterProofing.SLDPRT
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

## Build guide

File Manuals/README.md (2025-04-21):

This folder contains the assembly and operations manual.
The assembly manual describes assembling the physical system once you have manufactured all the parts.
The operations manual covers the software functions: programming and recalling a saved position or function.

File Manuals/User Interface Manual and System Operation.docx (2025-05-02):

User Interface Manual and System Operation

# Table of Contents:

# Summary

This document describes the functions of the user interface and contains operation instructions for operating team 205’s assistive robotic aid. There are eight interactable systems on the instrument panel: the joystick, two switches, and five buttons. The joystick is a three axis joystick, with two buttons on top for additional manipulation of the robotic arm. The switches are used as a system enable and a joystick enable, and the five buttons are used to save specific functions for the robotic arm. Together, these systems allow the user to manually control the robotic arm including pitching the end effector, as well as programming and recalling specific locations of high value to the user.

To access tutorial videos, use the QR code below and navigate to the “Tutorial Videos” folder. Find the video that corresponds to the correct instructions below. The tutorial videos are annotated and follow the same procedure as described below.

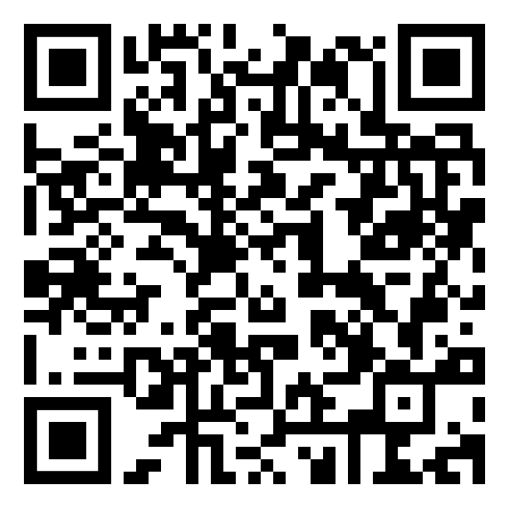
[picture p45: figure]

# User Interface

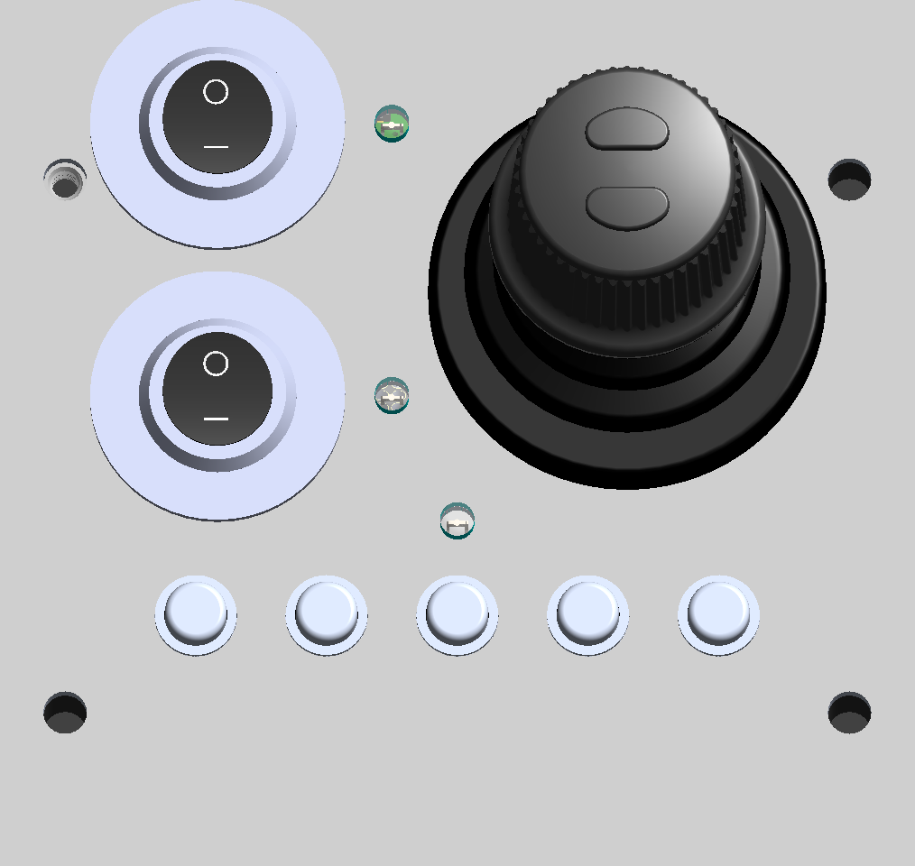
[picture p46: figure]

Joystick Buttons

Switch 2 (S2)

Switch 1 (S1)

LED 1 (LED1)

LED 2 (LED2)

Button 5 (B5)

Button 4 (B4)

Button 3 (B3)

Button 2 (B2)

Button 1 (B1)

Joystick 1 (JSTK1)

LED 3 (LED3)

Figure 1. Physical User Interface

Joystick 1 (JSTK 1): JSTK 1 is used to manually control the robotic arm, where forward-backward movement of the joystick corresponds to forward-backward movement of the robotic arm, left-right movement of the joystick correspond to left-right movement of the robotic arm, and twisting of the joystick corresponds to up-down movement of the robotic arm (see S. Joystick Control).

Switch 1 (S1): S1 is used to change the system state from static into joystick control mode. When the system is in static mode, the joystick and buttons are inoperable, and the software is not running any commands. When the system is in joystick control mode, the joystick and buttons are operational and normal movement occurs.

Switch 2 (S2): S2 is used to enable and disable the joystick for safety purposes. S2 mounts between the power from the ESP32 to the joystick, completely removing energy from the joystick when switched off.

Button 1 (B1): B1 is used as the unstow/ready/home function for the robotic arm. Pushing B1 will cause the arm to move from its current position to its defined “home” position.

Button 2 (B2): B2 is used to program and run the drinking function. When programming, the system will require the user to save four point that will designate the path from the drink to the user. After programming the function, pushing B2 will path to the drink, and move through the saved positions to the user, then back to the drink location.

Button 3 (B3): B3 is used to program and put the arm in stow1 position. Pushing B3 will cause the arm to move through a linear path from its current position to its stow1 position.

Button 4 (B4): B4 is used to program and put the arm in its stow2 position. Pushing B4 will cause the arm to move through a linear path from its current position to its stow2 position.

Button 5 (B5): B5 is used to operate the LED located on the end effector of the robot.

~~LED 1 (LED1):~~ ~~LED1 indicates~~ ~~the system status, if LED1 is lit up, the system is operational. If the LED is off, then the system is not operational, but is still powered on.~~

~~LED 2 (LED2):~~ ~~LED2 indicates whether JSTK1 is receiving power. If LED2 is lit up, the joystick is receiving power. If the LED is off, then only the joystick has been disconnected from power.~~

*LED 1 and 2 were removed from the final prototype as they were causing electrical issues that could not be resolved*

LED 3 (LED3): LED3 is the indicator for the buttons, showing which mode the system is in and specifically what part of the function the system is in. LED3 behavior will be described more in “Button Functions” Section

# Operating the System

Powering on the system:

- To power on the system, flip the switch on the battery to the “I” state (so that the “I” is depressed).
- The robotic arm will now run through setup code to go to an initial “ready position”. Please ensure that the immediate space around the robotic arm is clear to prevent any interruption.
- Once the robot arm has stopped moving and LED3 blinks briefly, the setup has been completed.

Operating the system:

- Once the setup has been completed, switch S1 to the on position (such that the “I” is depressed). The buttons are now operational.
- Switch S2 to the on position (such that the “I” is depressed).
- The joystick is now operational, ~~both~~ ~~LED1~~ ~~and~~ ~~LED2~~ ~~should be lit~~. The system is now fully operational and should be treated as such.

Powering off the system:

- Move the robot to the location to be stored at (ideally, programming B3 to be the stow position when turned off saves time and simplifies the power off process).
- Switch S2 to the off position (such that the “0” is depressed). The joystick is now inoperable.
- Switch S1 to the off position (such that the “0” is depressed). The buttons are now inoperable.
- Switch the power switch on the battery to the off position (such that the “0” is depressed). The system is now powered off.
- Note that there are rubber bands on the robotic arm that are used as dampeners during motion. When the system is completely switched off, these rubber bands may cause motion due to the elastic properties. It is recommended that either the stow1 or stow2 positions be programmed to a location where the rubber bands are maximally stretched or minimally stretched.

# Joystick Control

Twisting the top of the joystick clockwise will move the arm up (+Z)

Twisting the top of the joystick counterclockwise will move the arm down (-Z)

+X

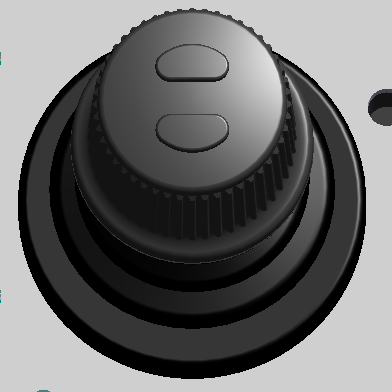
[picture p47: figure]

Open the end effector

Close the end effector

-Y

+Y

-X

# Button Functions

B1: Button 1 is used to program and recall the ready/home position.

To save a position:

1. Hold B1 for five seconds (count in your head) then release
2. LED3 will begin flashing after two seconds
3. The system is now in “Programming” mode
4. Using the joystick, move the arm into the position that you would like to save for the ready/home position
5. Push B1 briefly then release to save this position, LED3 will go static for one second, then turn off
6. The position for B1 has now been saved in the memory for later recall
7. The system is now in joystick control mode and can be normally operated

To recall the ready/home position:

1. Push B1 for one second or less, then release
2. LED3 will go static, and the arm will move to the previously saved position for the ready/home position, the joystick is inoperable during this movement
3. Once at the saved position, LED3 will turn off, and the system will return to joystick control mode and operate normally

B2: Button 2 is used to program and run the drink function.

To program the drink function:

1. Hold B2 for five seconds (count in your head) then release
2. LED3 will begin flashing after two seconds
3. The system is now in “Programming” mode
4. Using the joystick, move the arm to the position of the portable cupholder that contains the drink such that the top if the handle is resting inside the end effector of the robot
5. Push B2 briefly then release to save the drink position, LED3 will go static for one second, then continue flashing
6. Using the joystick, move the arm to a first safe position that extends outside the dimensions of the case. Assuming the system is mounted on the lefthand side of the chair, it is recommended that the first safe position be forward and left of the system

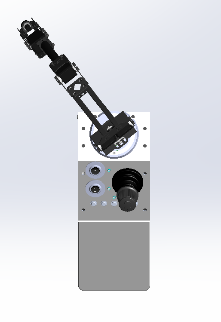
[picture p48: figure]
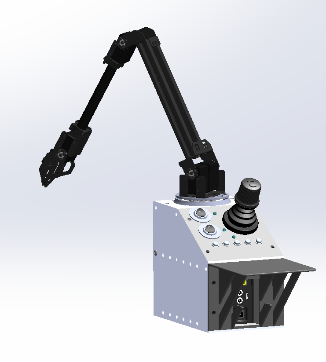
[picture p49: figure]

7. Push B2 briefly then release to save the “safe1” position, LED3 will go static for one second, then continue flashing

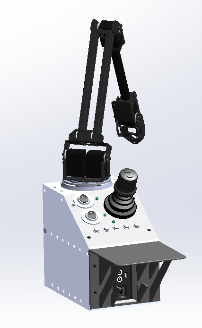
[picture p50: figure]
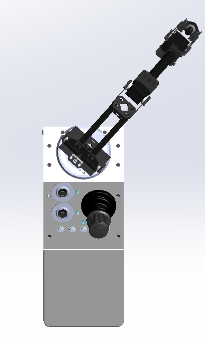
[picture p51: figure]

8. Using the joystick, move the arm to a second safe position that extends outside the dimensions of the case. Assuming the system is mounted on the lefthand side of the chair, it is recommended that the second safe position be forward and right of the system
9. Push B2 briefly then release to save the “safe2” position, LED3 will go static for one second, then continue flashing
10. Using the joystick, move the arm in front of the user where the drink should end up
11. Push B2 briefly then release to save the “user” position, LED3 will go static for one second, then turn off
12. You have now saved the path that the drink function will take when it is called. The drink will pass through the four points saved during this process, please ensure that there is adequate clearance for the drink to pass through these points. If there is not, restart the process at Step 1 to resave new positions for these four points

To run the drink function:

It is recommended that the robot be positioned in its ready/home position before running the drink function. The robot always moves linearly between two points and is not equipped with obstacle avoidance. Before running the drink function, ensure the path between the current position and the first safe position that was previously programmed is not obstructed.

1. Push B2 for one second or less, then release
2. LED3 will go static, and the arm will initially move to the “safe1” position
3. Next, the arm will move 200 mm above the “drink” location and open the end effector. Then the arm will move down to secure the handle in the end effector. The arm will then move back up 200 mm above the “drink” location
4. The arm will move to the “safe1” position
5. The arm will move to the “safe2” position
6. The arm will move to the “user” position. At this point, the arm will stop moving. The position can now be adjusted using the joystick in the event that the saved position is too far away from the user. Please note that at this time, the system is still operating within the drink function and is not in normal joystick control mode, it is only allowing the user to adjust the drink position around their face for these moments.
7. Once the user is finished drinking, push B2 briefly, then release
8. The arm will move to the “safe2” position
9. The arm will move to the “safe1” position
10. The arm will move 200 mm above the “drink” position. At this point the arm will stop moving. The position can now be adjusted using the joystick in the event that the portable cupholder is not aligned with the cupholder on the chair. IF THE POSITION IS ADJUSTED, THE CUP MUST BE MANUALLY LOWERED INTO THE CUPHOLDER USING THE JOYSTICK. Please note that at this time, the system is still operating within the drink function and is not in normal joystick control mode, it is only allowing the user to adjust the position for these moments.
11. Push B2 briefly, then release. The arm will move to the originally programmed “drink” location. If you made adjustments in the last step and manually moved the portable cupholder into the wheelchair mounted cupholder, then this operation should return the handle to the saved position. If you did not make any adjustments in step 10, then the robot will lower the portable cupholder in the cupholder mounted on the wheelchair.
12. The robot open the end effector to release the portable cupholder, then move up 200mm
13. The arm will move to the “safe1” position
14. The drink function is now complete and the system has returned to normal joystick control mode. It is recommended to push B1 and return the arm to the ready position before operating the system

B3: Button 3 is used to program and recall the Stow1 position.

To save a position:

8. Hold B3 for five seconds (count in your head) then release
9. LED3 will begin flashing after two seconds
10. The system is now in “Programming” mode
11. Using the joystick, move the arm into the position that you would like to save for the “stow1” position
12. Push B3 briefly then release to save this position, LED3 will go static for one second, then turn off
13. The position for B3 has now been saved in the memory for later recall
14. The system is now in joystick control mode and can be normally operated

To recall the ready/home position:

4. Push B3 for one second or less, then release
5. LED3 will go static, and the arm will move to the previously saved position for the “stow1” position, the joystick is inoperable during this movement
6. Once at the saved position, LED3 will turn off, and the system will return to joystick control mode and operate normally

B4: Button 4 is used to program and recall the Stow2 position.

To save a position:

15. Hold B4 for five seconds (count in your head) then release
16. LED3 will begin flashing after two seconds
17. The system is now in “Programming” mode
18. Using the joystick, move the arm into the position that you would like to save for the “stow2” position
19. Push B4 briefly then release to save this position, LED3 will go static for one second, then turn off
20. The position for B4 has now been saved in the memory for later recall
21. The system is now in joystick control mode and can be normally operated

To recall the ready/home position:

7. Push B4 for one second or less, then release
8. LED3 will go static, and the arm will move to the previously saved position for the “stow2” position, the joystick is inoperable during this movement
9. Once at the saved position, LED3 will turn off, and the system will return to joystick control mode and operate normally

B5: Button 5 is used to turn on and off the end effector LED

B5 is used to toggle the LED on and off. Pushing B5 will turn the LED on. Pushing B5 again will turn the LED off. Unlike the other buttons, LED3 will not turn on.

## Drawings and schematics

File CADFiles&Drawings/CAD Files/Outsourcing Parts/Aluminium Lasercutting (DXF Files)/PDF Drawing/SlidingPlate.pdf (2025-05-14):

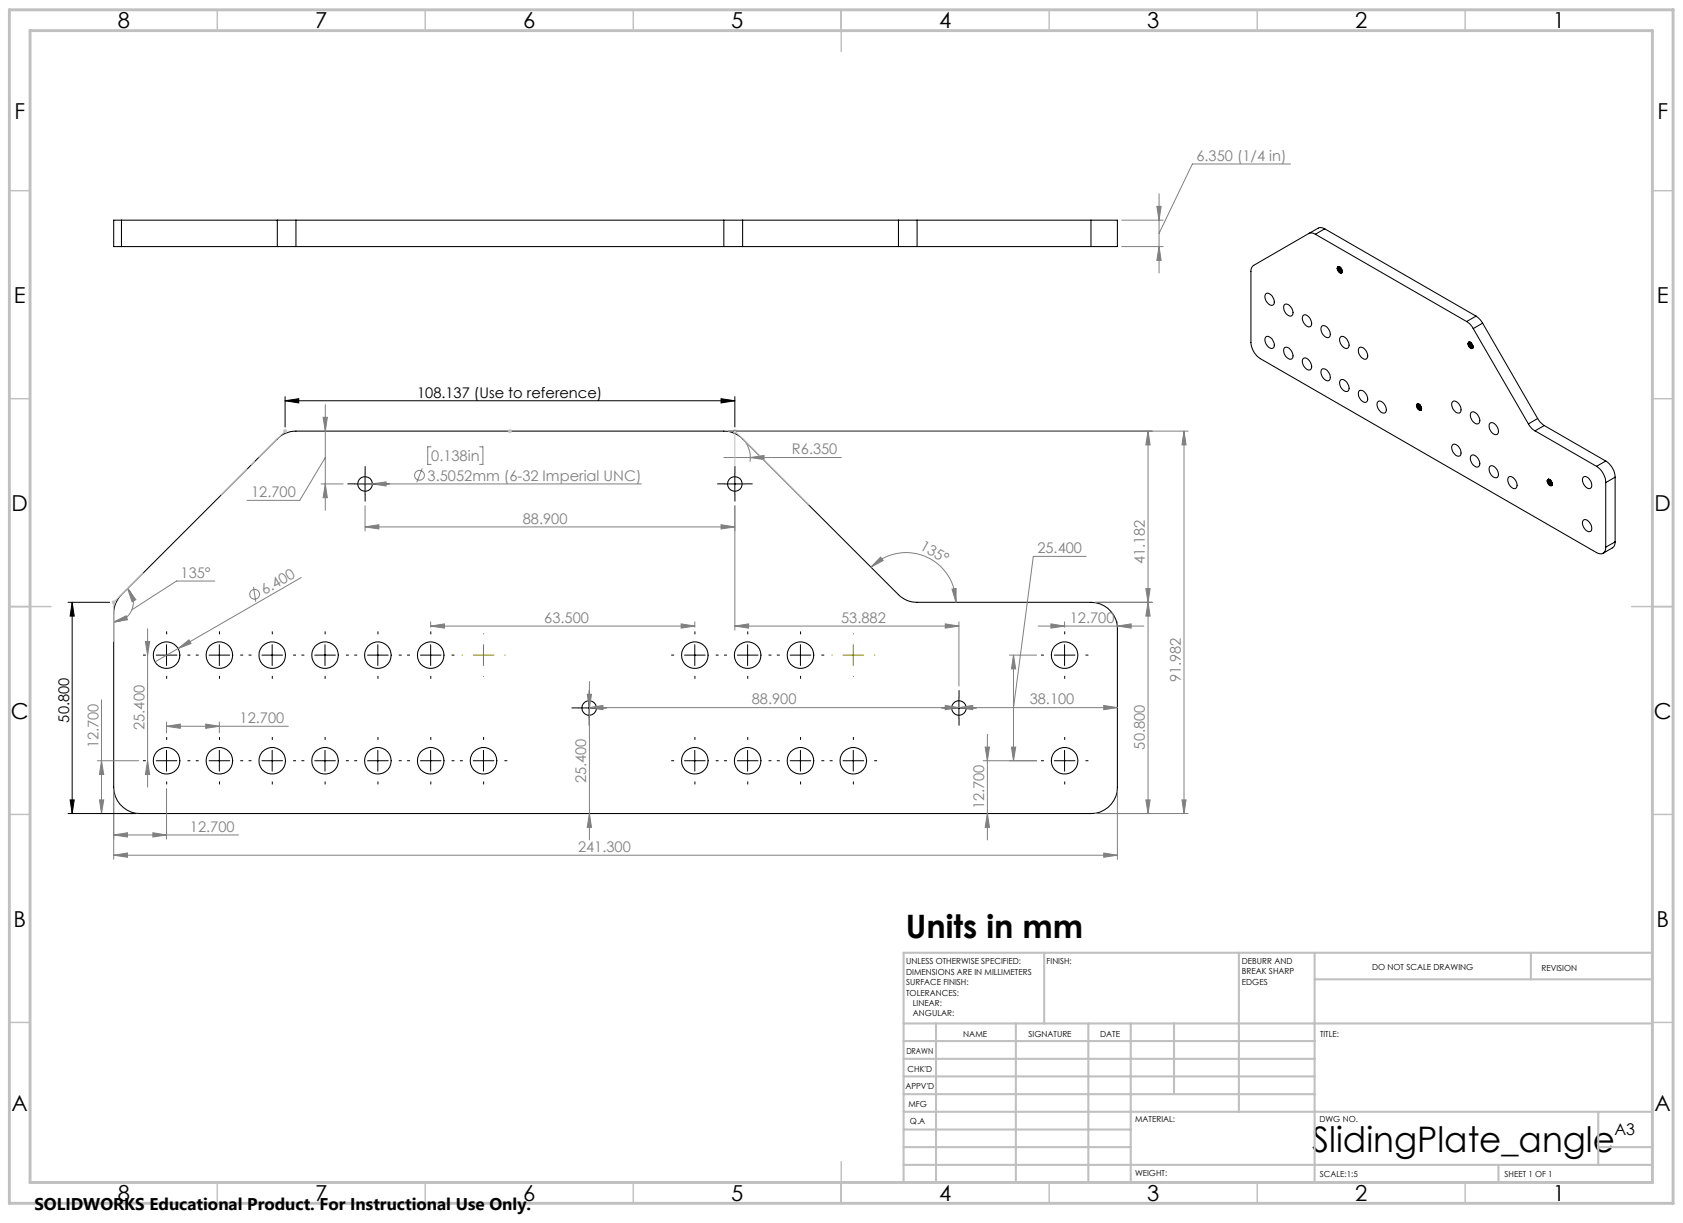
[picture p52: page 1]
3.5052mm (6-32 Imperial UNC); FINISH:; DEBURR AND; BREAK SHARP; DO NOT SCALE DRAWING; REVISION; SCALE:1:5; SHEET 1 OF 1

108.137 (Use to reference)

Units in mm

UNLESS OTHERWISE SPECIFIED:
DIMENSIONS ARE IN MILLIMETERS
SURFACE FINISH:
TOLERANCES:
LINEAR:
ANGULAR:

NAME | SIGNATURE | DATE | | | | TITLE:

DRAWN
CHK'D
APPV'D
MFG
Q.A | | | | MATERIAL: | DWG NO. SlidingPlate_angle | A3

SOLIDWORKS Educational Product. For Instructional Use Only.

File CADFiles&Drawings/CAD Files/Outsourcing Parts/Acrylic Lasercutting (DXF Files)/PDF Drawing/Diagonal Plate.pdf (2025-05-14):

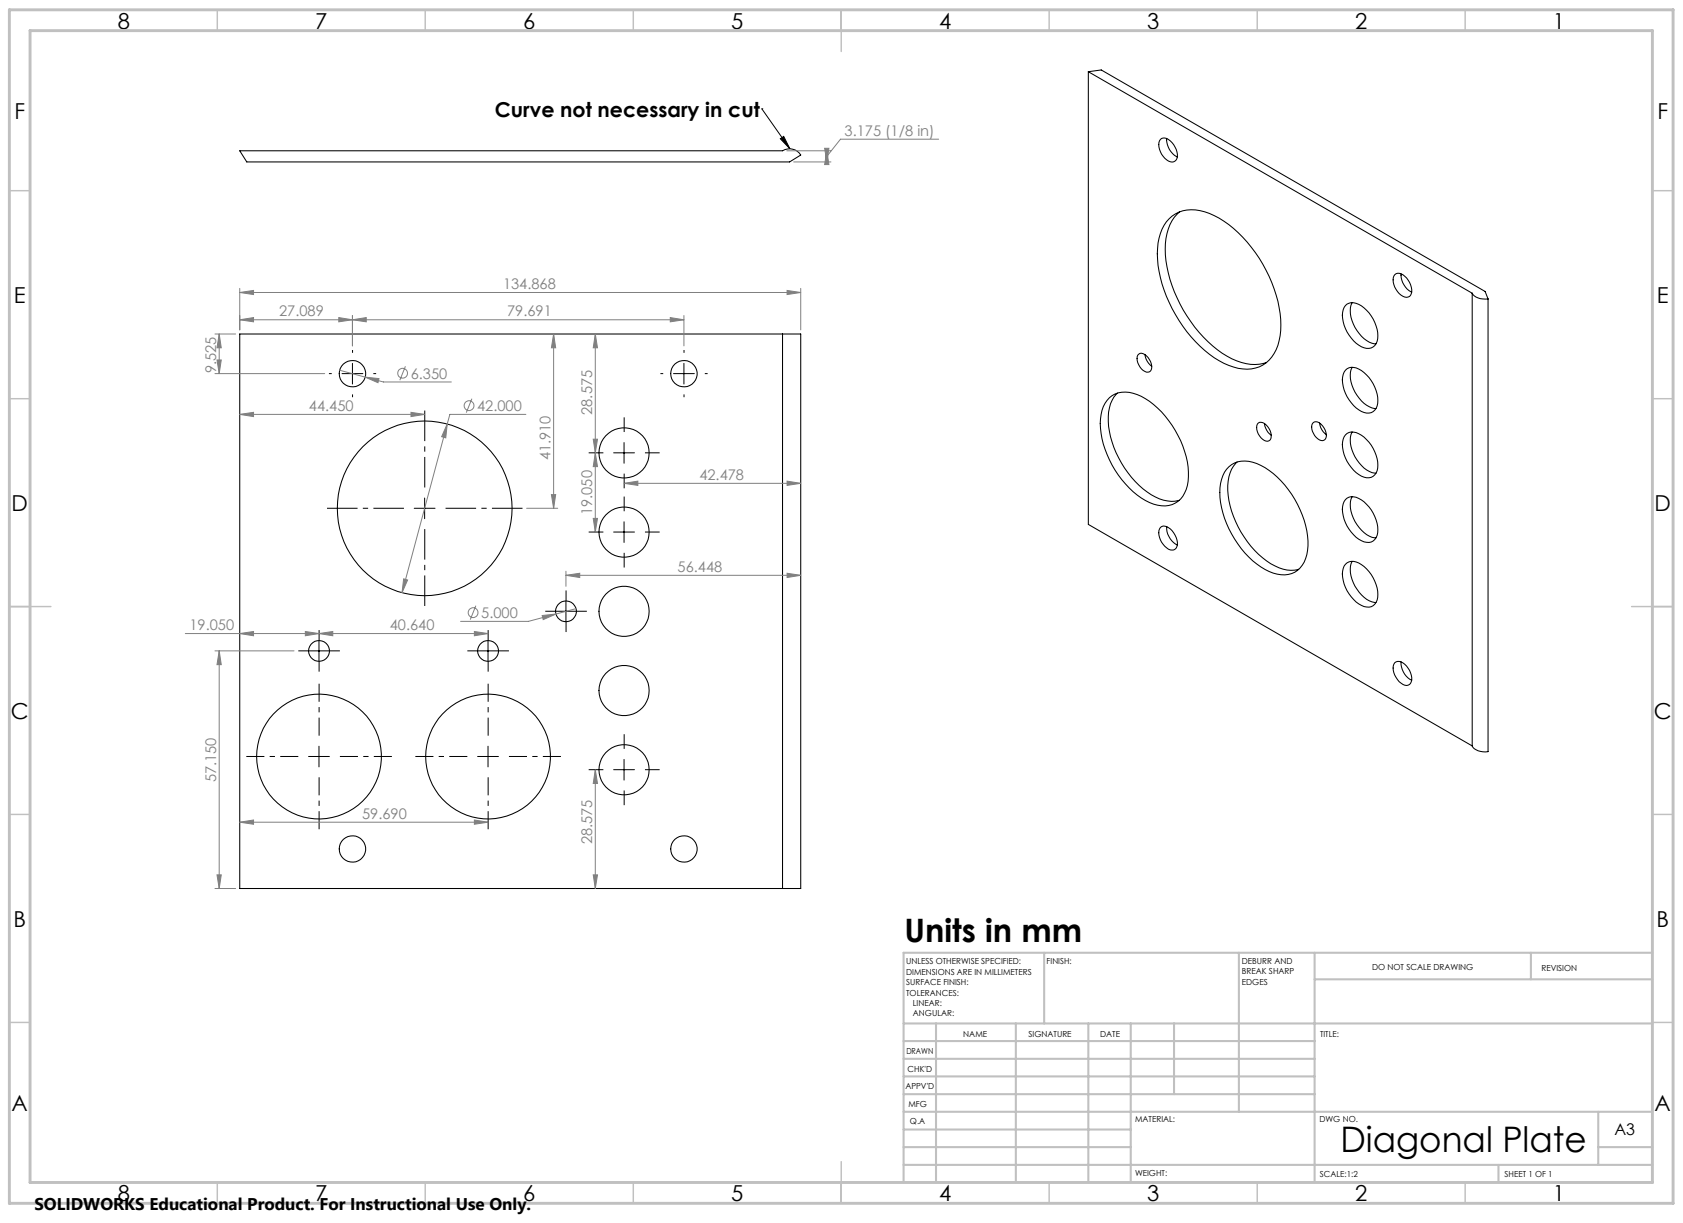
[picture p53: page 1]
FINISH:; DEBURR AND; BREAK SHARP; DO NOT SCALE DRAWING; REVISION; SCALE:1:2; SHEET 1 OF 1

Curve not necessary in cut

Units in mm

UNLESS OTHERWISE SPECIFIED:
DIMENSIONS ARE IN MILLIMETERS
SURFACE FINISH:
TOLERANCES:
LINEAR:
ANGULAR:

NAME | SIGNATURE | DATE | | | | TITLE:

DRAWN
CHK'D
APPV'D
MFG
Q.A | | | | MATERIAL: | DWG NO. Diagonal Plate | A3

SOLIDWORKS Educational Product. For Instructional Use Only.

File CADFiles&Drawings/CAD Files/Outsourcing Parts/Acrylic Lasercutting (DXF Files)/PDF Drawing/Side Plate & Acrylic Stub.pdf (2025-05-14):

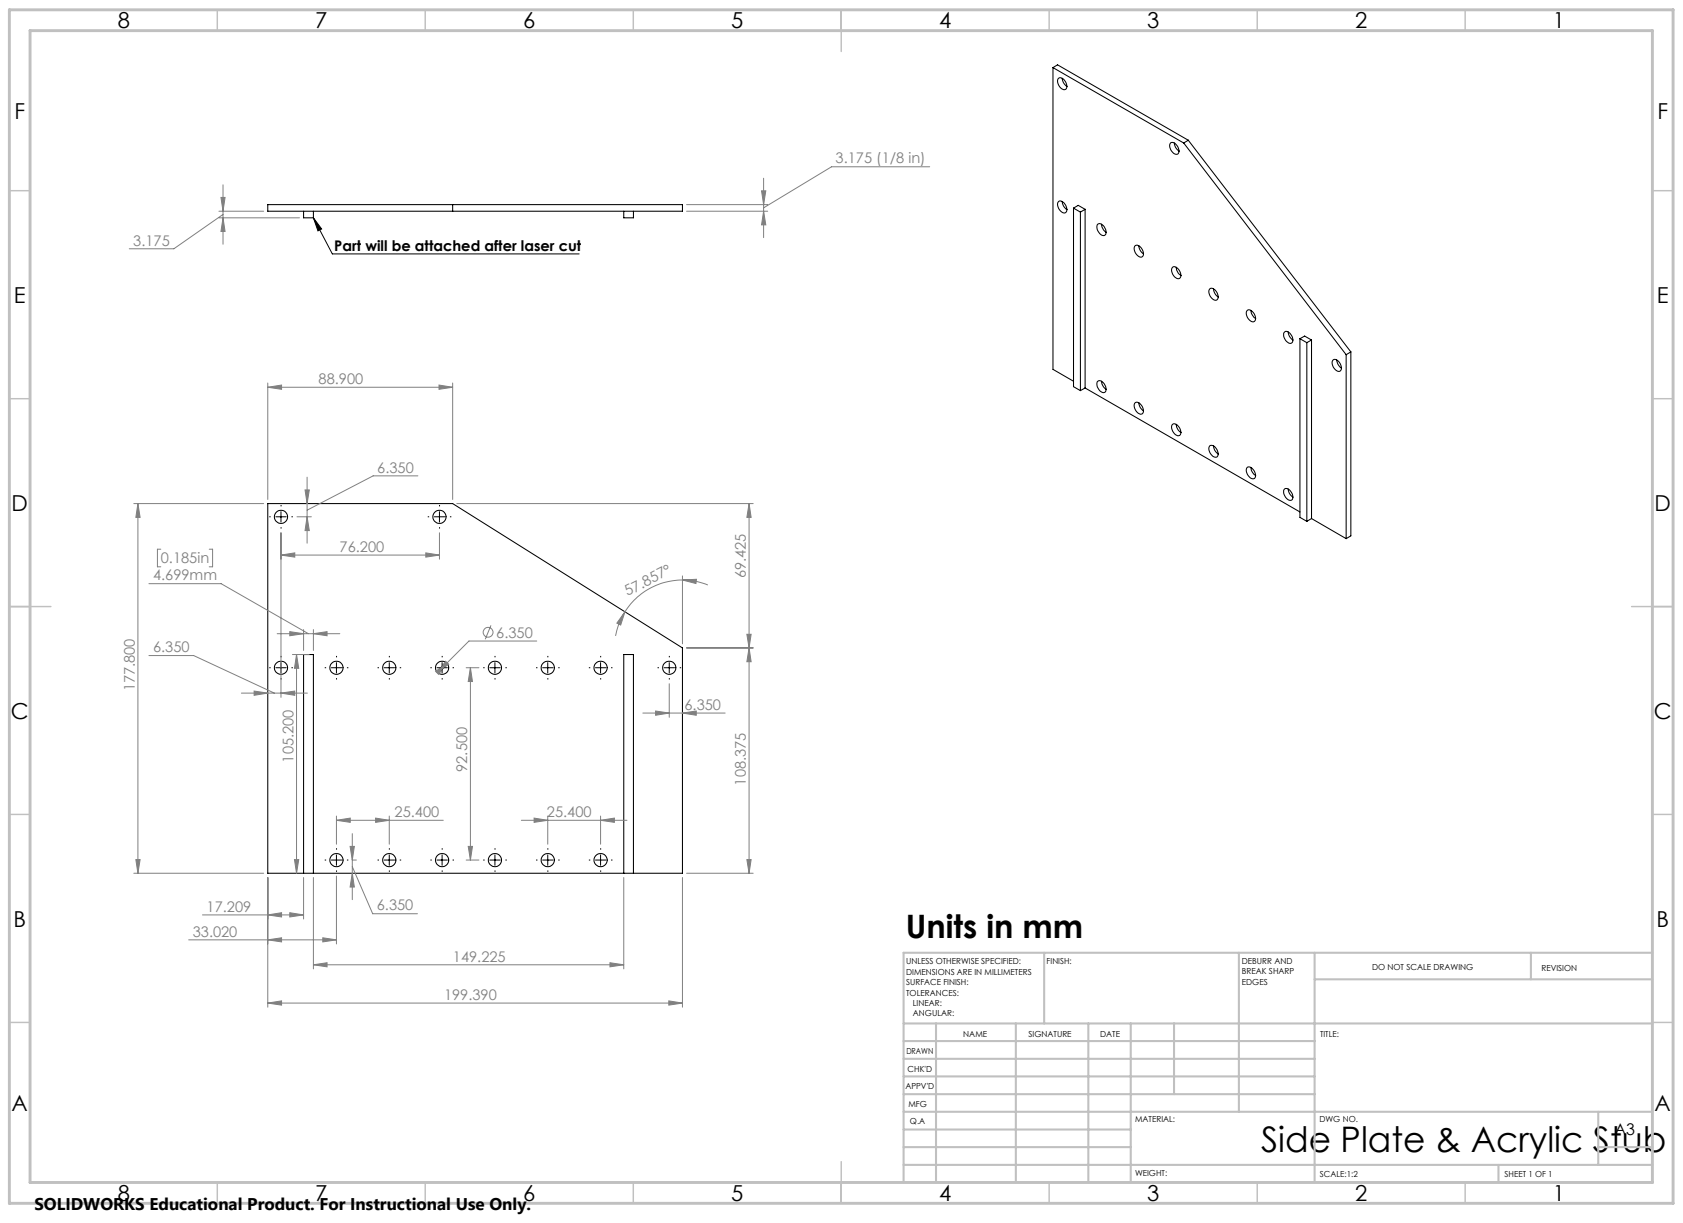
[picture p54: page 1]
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

Part will be attached after laser cut

Units in mm

UNLESS OTHERWISE SPECIFIED:
DIMENSIONS ARE IN MILLIMETERS
SURFACE FINISH:
TOLERANCES:
LINEAR:
ANGULAR:

NAME | SIGNATURE | DATE | | | | TITLE:

DRAWN
CHK'D
APPV'D
MFG
Q.A | | | | MATERIAL: Side Plate & Acrylic Stub | DWG NO. | A3

SOLIDWORKS Educational Product. For Instructional Use Only.

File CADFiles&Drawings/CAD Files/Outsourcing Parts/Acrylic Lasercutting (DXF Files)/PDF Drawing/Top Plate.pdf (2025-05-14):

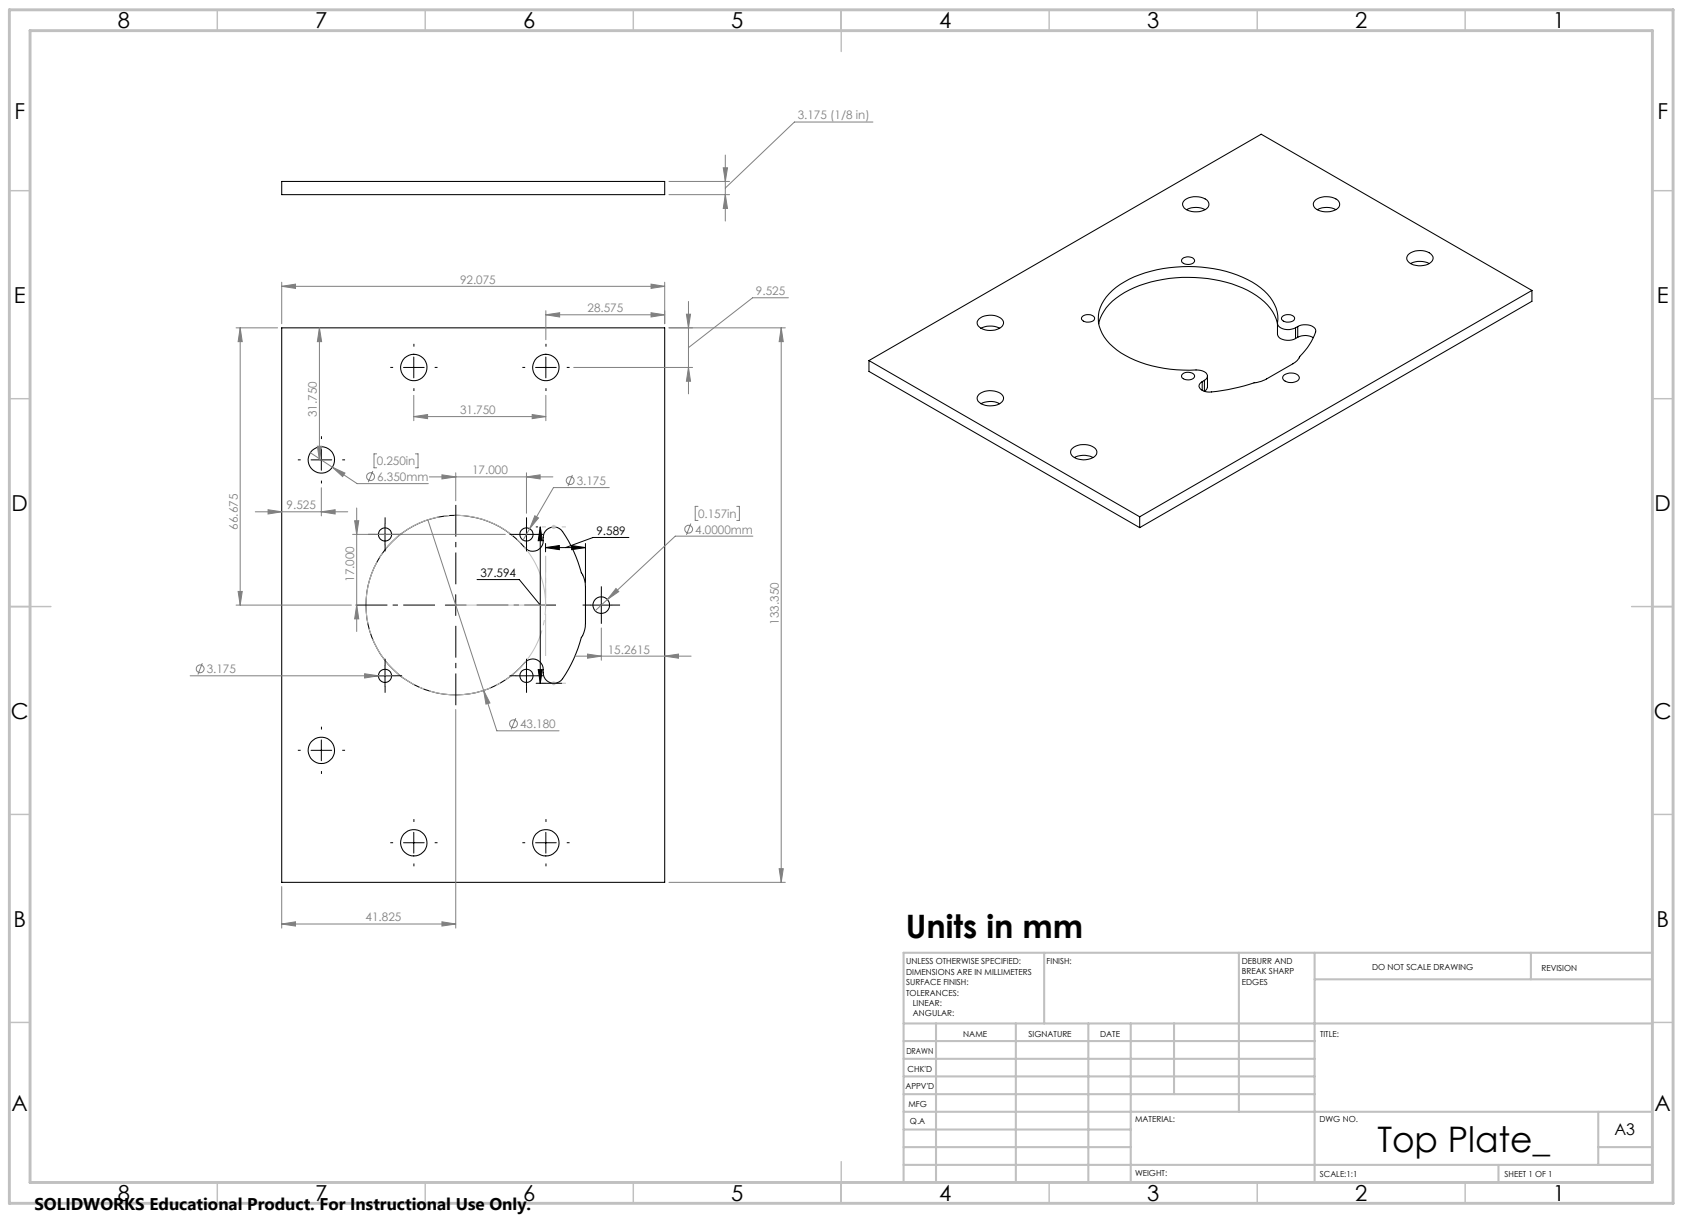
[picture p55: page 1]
FINISH:; DEBURR AND; BREAK SHARP; DO NOT SCALE DRAWING; REVISION; SCALE:1:1; SHEET 1 OF 1

Units in mm

UNLESS OTHERWISE SPECIFIED:
DIMENSIONS ARE IN MILLIMETERS
SURFACE FINISH:
TOLERANCES:
LINEAR:
ANGULAR:

NAME | SIGNATURE | DATE | | | | TITLE:

DRAWN
CHK'D
APPV'D
MFG
Q.A | | | | MATERIAL: | DWG NO. Top Plate_ | A3

SOLIDWORKS Educational Product. For Instructional Use Only.

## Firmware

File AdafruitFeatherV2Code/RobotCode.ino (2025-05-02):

// For internal pull down resistors, button state == High means that the button is not being pushed
// and button state == low means the button is being pushed.
#include <ArduinoJson.h>
#include <Preferences.h>
#include <float.h>

// Digital Pin naming, Please dont change these, they correspond to the wiring diagram and are used in multiple places in the code
#define D0 14   //LED Pin
#define D1 32   //button 1
#define D2 15   //Button 2
#define D3 33   //Button 3
#define D4 27   //Button 4
#define D5 12   //Button 5
#define D6 13   //Joystick Button 1
#define D7 37   //Joystick Button 2

unsigned long sleeptime = 10000;  // Microseconds -- What is this for

unsigned long currentJstkMillis; //Millis function specific for joystick
unsigned long lastJstkUpdate = 0; //Time at which the currentJstkMillis was >= 25ms.
const unsigned long JstkUpdateInterval = 40; //Interval time the Jstk should read values at a rate of 25ms.

// Declare our local coordinate variables on feather side
float curxpos, curypos, curzpos, curtpos;
float distance;


//Declare variables used for safety checks in joystick function
float varbuffz, deadzone;
const float caseMaxX = 20;
const float caseMinX = -310;
const float caseMaxY = 50;
const float caseMinY = -50;
const float caseMaxZ = 10;
const float caseMinZ = -190;
int safetybuff;

// Declare state variables to be used for the light
bool lightstate;

// Create the counters for all four buttons that require programming and recal capabilities
int debounceTimer = 50;
unsigned long minButtonHold = 3000; //Minimum hold time to start the "saving" funciton


int buttonStatePrevious1 = HIGH;  //Set initial button state to no click (OFF)
int button1 = HIGH;
unsigned long buttonLongPressMillis1; //Time in ms the button was pressed
bool buttonStateLongPress1 = false; 
unsigned long buttonPreviousMillis1;
unsigned long buttonPressDuration1;
unsigned long currentMillis1; //Variable to store the number of milliseconds since the Arduino has been turned on

int buttonStatePrevious2 = HIGH;  //Set initial button state to no click (OFF)
int button2 = HIGH;
unsigned long buttonLongPressMillis2; //Time in ms the button was pressed
bool buttonStateLongPress2 = false;  
unsigned long buttonPreviousMillis2;
unsigned long buttonPressDuration2;
unsigned long currentMillis2; //Variable to store the number of milliseconds since the Arduino has been turned on

int buttonStatePrevious3 = HIGH;  //Set initial button state to no click (OFF)
int button3 = HIGH;
unsigned long buttonLongPressMillis3; //Time in ms the button was pressed
bool buttonStateLongPress3 = false;  
unsigned long buttonPreviousMillis3;
unsigned long buttonPressDuration3;
unsigned long currentMillis3; //Variable to store the number of milliseconds since the Arduino has been turned on

int buttonStatePrevious4 = HIGH;  //Set initial button state to no click (OFF)
int button4 = HIGH;
unsigned long buttonLongPressMillis4; //Time in ms the button was pressed
bool buttonStateLongPress4 = false;  
unsigned long buttonPreviousMillis4;
unsigned long buttonPressDuration4;
unsigned long currentMillis4; //Variable to store the number of milliseconds since the Arduino has been turned on

// Variables for if button 5 is to be used as an extra saved position rather than the end effector LED
// Uncomment below if you intend to use the extra button function:

// int buttonStatePrevious5 = HIGH;  //Set initial button state to no click (OFF)
// int button5 = HIGH;
// unsigned long buttonLongPressMillis5; //Time in ms the button was pressed
// bool buttonStateLongPress5 = false;  
// unsigned long buttonPreviousMillis5;
// unsigned long buttonPressDuration5;
// unsigned long currentMillis5; //Variable to store the number of milliseconds since the Arduino has been turned on


void setup() {
  Serial1.begin(115200);
  Serial.begin(115200);

  // Set Pinmodes
  // Analog Pins:
  pinMode(A0, INPUT);  // Joystick X Input
  pinMode(A1, INPUT);  // Joystick Y Input
  pinMode(A2, INPUT);  // Joystick Z Input
  pinMode(A3, INPUT);  // Switch Logic input for joystick
  pinMode(A4, INPUT);  // Switch Logic input for system enable
  // Digital Pins:
  pinMode(D0, OUTPUT);        // Status LED
  pinMode(D1, INPUT_PULLUP);  // Panel Button 1
  pinMode(D2, INPUT_PULLUP);  // Panel Button 2
  pinMode(D3, INPUT_PULLUP);  // Panel Button 3
  pinMode(D4, INPUT_PULLUP);  // Panel Button 4
  pinMode(D5, INPUT_PULLUP);  // Panel Button 5
  pinMode(D6, INPUT_PULLUP);  // Joystick Button 1
  pinMode(D7, INPUT_PULLUP);  // Joystick Button 2

  // Check for the status of the serial 1, ESP 32 has startup code it needs to run, we need to know when we get connection and can send commands
  Serial.println("Attempting to connect to serial1...");
  while(!Serial1.available()) {
    delay(100);
    Serial.print("Waiting for connection .");
    delay(300);
    Serial.print(" .");
    delay(300);
    Serial.print(" .");
    delay(300);
    Serial.println();
  }
  Serial.println("Serial1 Connection Established");
  delay(2000);

  // Move to our initial postion that we define
  curxpos = 150;
  curypos = 0;
  curzpos = 150;
  curtpos = 3.24;
  lightstate = true;
  StaticJsonDocument<200> curposdoc;
  curposdoc["T"] = 1041;
  curposdoc["x"] = curxpos;
  curposdoc["y"] = curypos;
  curposdoc["z"] = curzpos;
  curposdoc["t"] = curtpos;
  serializeJson(curposdoc, Serial1);
  Serial1.println();
  Serial.println("Moving to Initial position . . . ");
  delay(1500);

  // Grab the feedback from the robotic arm to sync up local coordinate with robot coordinate
  StaticJsonDocument<200> initdoc;
  initdoc["T"] = 105;
  serializeJson(initdoc, Serial1);
  Serial1.println();
  delay(100);
  String response = Serial1.readStringUntil('\n');
  StaticJsonDocument<200> responseDoc;
  DeserializationError error = deserializeJson(responseDoc, response);
  if (!error) {
    curxpos = responseDoc["x"];
    curypos = responseDoc["y"];
    curzpos = responseDoc["z"];
    curtpos = responseDoc["t"];
  }
  String syncinfo = String(curxpos) + " " + String(curypos) + " " + String(curzpos) + " " + String(curtpos);
  Serial.println(syncinfo);
  Serial.println("The feather and robot coordinates have been synced");
  delay(1500);
}

// Define key functions for use later in the main loop:

void ledblinker() { // Flashing LED when in programming mode
  digitalWrite(D0, HIGH);
  delay(10);
  digitalWrite(D0, LOW);
  delay(10);
}

void IsInsideCase() {
  safetybuff = 5;

  bool inside = (curxpos >= caseMinX && curxpos <= caseMaxX &&
                 curypos >= caseMinY && curypos <= caseMaxY &&
                 curzpos >= caseMinZ && curzpos <= caseMaxZ);

  if (inside) {
    // Calculate distances to each boundary
    float xdistToMin = abs(curxpos - caseMinX);
    float xdistToMax = abs(curxpos - caseMaxX);
    float ydistToMin = abs(curypos - caseMinY);
    float ydistToMax = abs(curypos - caseMaxY);
    float zdistToMin = abs(curzpos - caseMinZ);
    float zdistToMax = abs(curzpos - caseMaxZ);

    // Find minimum distance and direction
    float minDist = xdistToMin;
    char axis = 'x';
    int dir = -1;

    if (xdistToMax < minDist) { minDist = xdistToMax; axis = 'x'; dir = 1; }
    if (ydistToMin < minDist) { minDist = ydistToMin; axis = 'y'; dir = -1; }
    if (ydistToMax < minDist) { minDist = ydistToMax; axis = 'y'; dir = 1; }
    if (zdistToMin < minDist) { minDist = zdistToMin; axis = 'z'; dir = -1; }
    if (zdistToMax < minDist) { minDist = zdistToMax; axis = 'z'; dir = 1; }

    // Apply correction only to the axis with minimum distance
    switch (axis) {
      case 'x':
        curxpos += dir * (minDist + safetybuff);
        break;
      case 'y':
        curypos += dir * (minDist + safetybuff);
        break;
      case 'z':
        curzpos += dir * (minDist + safetybuff);
        break;
    }

    // Send updated position
    StaticJsonDocument<200> curposdoc;
    curposdoc["T"] = 1041;
    curposdoc["x"] = curxpos;
    curposdoc["y"] = curypos;
    curposdoc["z"] = curzpos;
    curposdoc["t"] = curtpos;
    serializeJson(curposdoc, Serial1);
    Serial1.println();
    Serial.println("Correcting case bounds (minimal axis)");
    delay(50);
  }
}

void IsOutsideBounds(){ // SAFETY CHECK: Endure the arm does not exceed its phsyical limits
  if ((sqrt(sq(curxpos) + sq(curypos)) < 100) && curzpos > 0){ //Check the lower limits, dont let the arm go over the origin
    ledblinker();
    if (curxpos > 0){
      curxpos +=5;
    }
    if (curxpos < 0){
      curxpos -=5;
    }
    if (curypos > 0){
      curypos +=5;
    }
    if (curypos < 0){
      curypos -=5;
    }
    StaticJsonDocument<200> curposdoc;
    curposdoc["T"] = 1041;
    curposdoc["x"] = curxpos;
    curposdoc["y"] = curypos;
    curposdoc["z"] = curzpos;
    curposdoc["t"] = curtpos;
    serializeJson(curposdoc, Serial1);
    Serial1.println();
    Serial.println("Above the origin");
    delay(50);
  }
  if (distance > 498.99) { // Check the upper limits, dont let the arm go past its physical max reach
    ledblinker();
    delay(500);
    if (curxpos > 0){
      curxpos -= 5;
    }
    if (curxpos < 0){
      curxpos += 5;
    }
    if (curypos > 0){
      curypos -= 5;
    }
    if (curypos < 0){
      curypos += 5;
    }
    if (curzpos > 0){
      curzpos -= 2;
    }
    if (curzpos < 0){
      curzpos += 2;
    }

    StaticJsonDocument<200> curposdoc;
    curposdoc["T"] = 1041;
    curposdoc["x"] = curxpos;
    curposdoc["y"] = curypos;
    curposdoc["z"] = curzpos;
    curposdoc["t"] = curtpos;
    serializeJson(curposdoc, Serial1);
    Serial1.println();
    Serial.println("Exceeding the max distance bounds");
    delay(50);
  }
  else{
    return;
  }
}
void IsAboveHand(){ // SAFETY CHECK: Ensure the arm does not move above the persons hand
  const float theta1 = -150;  // Lower bound of restricted arc (in degrees)
  const float theta2 = 150; // Upper bound of restricted arc (in degrees)
  float theta_cur = atan2(curypos, curxpos) * 180.0 / PI;
  // Ensure arm does not enter the restricted arc
  if (theta_cur <= theta1 || theta_cur >= theta2) {
    // Move the arm to a safe angle
    if (theta_cur < 0) {
      theta_cur = theta1 + 6;  // Move slightly below restricted arc
    } else {
      theta_cur = theta2 - 6;  // Move slightly above restricted arc
    }
    // Convert back to Cartesian coordinates while maintaining current radius
    float radius = sqrt(sq(curxpos) + sq(curypos));
    curxpos = (radius + 1) * cos(theta_cur * PI / 180.0);
    curypos = (radius + 1) * sin(theta_cur * PI / 180.0);
    Serial.println("Above the Hand");
    StaticJsonDocument<200> curposdoc;
    curposdoc["T"] = 1041;
    curposdoc["x"] = curxpos;
    curposdoc["y"] = curypos;
    curposdoc["z"] = curzpos;
    curposdoc["t"] = curtpos;
    serializeJson(curposdoc, Serial1);
    Serial1.println();
    serializeJson(curposdoc, Serial);
    Serial.println();
    delay(50);
  }
  else{
    return;
  }
}
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
